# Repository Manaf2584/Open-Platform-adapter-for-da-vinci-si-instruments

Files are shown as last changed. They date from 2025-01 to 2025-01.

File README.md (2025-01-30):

# Bill of Materials

| Item Name | Quantity | Total Cost (£ - GBP) | Description |
|-----------|----------|----------------------|-------------|
| **Dynamixel XC330-M288-T** | 4 | 335.60 | Servo Motors |
| **Igus Linear Guide Carriage TW-04-15** | 2 | 57.98 | Secures servo motor grippers with the servo motors |
| **Igus Linear Guide Rail TS-04-15-600** | 1 | 40.66 | Secures all that is on the Carriage, 13mm |
| **OpenRB-150 Controller** | 1 | 29.10 | Microcontroller |
| **Compression Springs** | 4 | 11.48 | Dimensions: OD=9mm, FL=5mm, Th=0.8mm |
| **SparkFun Joystick** | 1 | 1.04 | Control system |
| **Solderable Breadboard** | 1 | 4.73 | Housed within the control module |
| **Saia-Burgess Plunger Micro Switch (Mfr Part No. 42393)** | 1 | 2.38 | Microswitch, used as a safety switch on the control module |
| **Bambu PLA** | - | - | Print material used for all components |
| **Miscellaneous** | - | 13.53 | 10 kΩ resistor, jumper wires, screws, nuts, heat shrink, thumb screws, and thread inserts |

**Grand Total:** £499.50 (Updated 30/01/2025)

Showcase video: https://youtu.be/XzJ7v7rmKO0

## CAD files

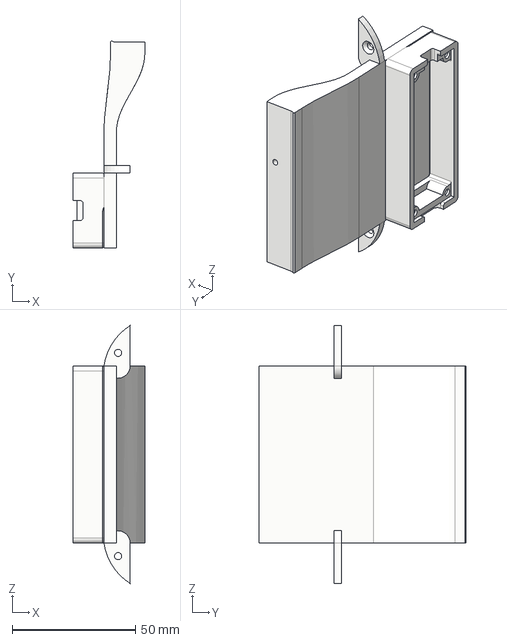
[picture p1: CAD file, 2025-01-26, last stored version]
R Wall.step
29.1 x 83.9 x 104.5 mm

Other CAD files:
R Wall.f3d

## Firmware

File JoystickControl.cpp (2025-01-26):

#include <Dynamixel2Arduino.h>   // Library for controlling Dynamixel motors
#include <tuple>                 // For std::tuple usage
using std::tuple;
using std::make_tuple;
using std::get;

#if defined(ARDUINO_OpenRB)  // If using the OpenRB-150 board
  #define DXL_SERIAL Serial1
  #define DEBUG_SERIAL Serial
  const int DXL_DIR_PIN = -1;
#endif

//----------------------------------
// Function Prototypes
//----------------------------------
tuple<int, int> homeMotor(int DXL_ID);
bool detectNoMovementWithinTurns(int DXL_ID, int delay_time, int no_movement_threshold, int movement_threshold, int max_position_units);
void calculateErrors(); // (Currently unused - for future error calculations)
int scaleToMotorRange(double angle, int cw_limit, int ccw_limit);
void initializeThetas();

//----------------------------------
// Joystick and Switch Configuration
//----------------------------------
const int JOYSTICK_X_PIN = A0;    // X-axis analog pin
const int JOYSTICK_Y_PIN = A1;    // Y-axis analog pin
const int JOYSTICK_SW_PIN = A2;   // Joystick switch pin
const int ENABLE_SWITCH_PIN = A3; // Additional switch pin

// Joystick center values and dead zones
const int JOYSTICK_CENTER_X = 732;
const int JOYSTICK_CENTER_Y = 756;
const int JOYSTICK_CENTER_RANGE_X_MIN = 731;
const int JOYSTICK_CENTER_RANGE_X_MAX = 733;
const int JOYSTICK_CENTER_RANGE_Y_MIN = 755;
const int JOYSTICK_CENTER_RANGE_Y_MAX = 757;
const int JOYSTICK_DEADZONE = 100;

// Control angles and increments
const float MAX_ANGLE_INCREMENT_ROLL_PITCH = 10.0; // deg/update
const float MAX_ANGLE_INCREMENT_JAWS = 10.0;       // deg/update
bool jawControlMode = false;                       // Toggles between roll/pitch mode and jaw mode
bool previousSWState = HIGH;                       // Tracks previous switch state

//----------------------------------
// Dynamixel Configuration
//----------------------------------
const uint8_t DXL_IDs[] = {1, 2, 3, 4};            // Motor IDs
const int NUM_MOTORS = sizeof(DXL_IDs) / sizeof(DXL_IDs[0]);
const float DXL_PROTOCOL_VERSION = 2.0;
const int DXL_BAUD_RATE = 57600;
Dynamixel2Arduino dxl(DXL_SERIAL, DXL_DIR_PIN);

//----------------------------------
// Motion and Safety Limits
//----------------------------------
using namespace ControlTableItem;
const int MAX_CURRENT = 170;  // Safe current limit for motors (in milliamps)
const float MAX_POSITION_RANGE = 600; // Max range in degrees (for safety)
const bool POSITIVE_IS_CCW = true;    // Rotation sign convention

// Arrays to store motor CW/CCW limits (updated after homing)
int cw_limits[NUM_MOTORS];
int ccw_limits[NUM_MOTORS];

//----------------------------------
// Transmission Matrix
//----------------------------------
// Maps user input (theta_R, theta_W, etc.) to motor angles
double transmissionMatrix[4][4] = {
  {0,    0,    0,    1.54},
  {0,    0,    1.03, 0   },
  {0,    1.15, -0.743,0  },
  {1.15, 0,    -0.743,0  }
};

// Inverse of the above matrix to compute motor angles from desired angles
double inverseMatrix[4][4] = {
  {0,               0.6272688898269312, 0,               0.8695652173913043},
  {0,               0.6272688898269312, 0.8695652173913043, 0             },
  {0,               0.970873786407767,  0,               0               },
  {0.6493506493506493, 0,               0,               0               }
};

//----------------------------------
// Angle Variables
//----------------------------------
double theta_R;  // Roll
double theta_W;  // Wrist (pitch)
double theta_G1; // Gripper half 1
double theta_G2; // Gripper half 2

//----------------------------------
// Loop Timing
//----------------------------------
unsigned long lastControlTime = 0;
const unsigned long controlInterval = 40; // in milliseconds

//----------------------------------
// Arduino Setup
//----------------------------------
void setup() {
  delay(1000);
  Serial.begin(57600);

  // Configure joystick and switches
  pinMode(JOYSTICK_SW_PIN, INPUT_PULLUP);
  pinMode(ENABLE_SWITCH_PIN, INPUT_PULLUP);
  previousSWState = digitalRead(JOYSTICK_SW_PIN);

  // Initialize Dynamixel
  dxl.begin(DXL_BAUD_RATE);
  dxl.setPortProtocolVersion(DXL_PROTOCOL_VERSION);

  // Homing sequence for each motor
  for (int i = 0; i < NUM_MOTORS; i++) {
    int DXL_ID = DXL_IDs[i];
    if (dxl.ping(DXL_ID)) {
      Serial.print("Dynamixel with ID: ");
      Serial.print(DXL_ID);
      Serial.println(" is connected!");

      // Set motor to Current Control Mode for homing
      dxl.torqueOff(DXL_ID);
      dxl.setOperatingMode(DXL_ID, OP_CURRENT);
      dxl.writeControlTableItem(CURRENT_LIMIT, DXL_ID, MAX_CURRENT);
      dxl.writeControlTableItem(HOMING_OFFSET, DXL_ID, 0);

      // Home this motor
      tuple<int, int> limits = homeMotor(DXL_ID);
      cw_limits[i] = get<0>(limits);
      ccw_limits[i] = get<1>(limits);
    } 
    else {
      Serial.print("Failed to connect to Dynamixel with ID: ");
      Serial.println(DXL_ID);
    }
  }

  // After homing, set motors to Current-Based Position Mode
  for (int i = 0; i < NUM_MOTORS; i++) {
    int DXL_ID = DXL_IDs[i];
    dxl.torqueOff(DXL_ID);
    dxl.setOperatingMode(DXL_ID, OP_CURRENT_BASED_POSITION);
    dxl.writeControlTableItem(CURRENT_LIMIT, DXL_ID, MAX_CURRENT);
    dxl.torqueOn(DXL_ID);
  }

  // Initialize thetas based on motor positions
  initializeThetas();
}

//----------------------------------
// Main Control Loop
//----------------------------------
void loop() {
  // Ensure the loop runs at a fixed interval
  if (millis() - lastControlTime >= controlInterval) {
    lastControlTime = millis();

    // Detect joystick switch press to toggle jaw mode
    bool currentSWState = digitalRead(JOYSTICK_SW_PIN);
    if (previousSWState == HIGH && currentSWState == LOW) {
      jawControlMode = !jawControlMode;
      Serial.print("Jaw control mode: ");
      Serial.println(jawControlMode ? "ON" : "OFF");
    }
    previousSWState = currentSWState;

    // Read enable switch and joystick
    bool enableSwitchState = digitalRead(ENABLE_SWITCH_PIN);
    int joystickX = analogRead(JOYSTICK_X_PIN);
    int joystickY = analogRead(JOYSTICK_Y_PIN);

    // Check if joystick is near center
    bool isJoystickCentered = 
        (joystickX >= JOYSTICK_CENTER_RANGE_X_MIN && joystickX <= JOYSTICK_CENTER_RANGE_X_MAX) &&
        (joystickY >= JOYSTICK_CENTER_RANGE_Y_MIN && joystickY <= JOYSTICK_CENTER_RANGE_Y_MAX);

    // Only process joystick if switch is not pressed and joystick is not centered
    if (enableSwitchState == HIGH && !isJoystickCentered) {
      int xDeviation = joystickX - JOYSTICK_CENTER_X;
      int yDeviation = joystickY - JOYSTICK_CENTER_Y;

      // Apply deadzone
      if (abs(xDeviation) < JOYSTICK_DEADZONE) xDeviation = 0;
      if (abs(yDeviation) < JOYSTICK_DEADZONE) yDeviation = 0;

      // Update angles if there's significant deviation
      if (xDeviation != 0 || yDeviation != 0) {
        const float MAX_JOYSTICK_DEVIATION = 512 - JOYSTICK_DEADZONE;
        float xAngleIncrement, yAngleIncrement;

        // If jaws are controlled, only horizontal is used by default
        if (jawControlMode) {
          xAngleIncrement = ((float)xDeviation / MAX_JOYSTICK_DEVIATION) * MAX_ANGLE_INCREMENT_JAWS;
          yAngleIncrement = 0; // No vertical by default in jaws mode
        } else {
          // Roll/Pitch control
          xAngleIncrement = ((float)xDeviation / MAX_JOYSTICK_DEVIATION) * MAX_ANGLE_INCREMENT_ROLL_PITCH;
          yAngleIncrement = ((float)yDeviation / MAX_JOYSTICK_DEVIATION) * MAX_ANGLE_INCREMENT_ROLL_PITCH;
        }

        // Update angles based on current mode
        if (jawControlMode) {
          // Jaws: open/close with horizontal movement
          theta_G1 -= xAngleIncrement; 
          theta_G2 += xAngleIncrement;

          // If vertical input is desired for jaws, shift both jaws
          if (yDeviation != 0) {
            float yJawIncrement = ((float)yDeviation / MAX_JOYSTICK_DEVIATION) * MAX_ANGLE_INCREMENT_JAWS;
            double jawsMid = (theta_G1 + theta_G2) / 2.0;
            double jawsHalfGap = (theta_G2 - theta_G1) / 2.0;
            jawsMid += yJawIncrement;
            theta_G1 = jawsMid - jawsHalfGap;
            theta_G2 = jawsMid + jawsHalfGap;
          }

        } else {
          // Roll (theta_R) and Pitch (theta_W)
          theta_R += xAngleIncrement;
          theta_W += yAngleIncrement;
        }

        // Enforce a minimum gap between G1 and G2
        if (theta_G2 > theta_G1) {
          float midAngle = (theta_G1 + theta_G2) / 2;
          theta_G1 = midAngle - 15; 
          theta_G2 = midAngle + 15;
        }

        // Constrain angles to avoid physical damage
        theta_R = constrain(theta_R, -90, 90);
        theta_W = constrain(theta_W, -95, 95);
        theta_G1 = constrain(theta_G1, -200, 190);
        theta_G2 = constrain(theta_G2, -190, 200);
      }
    }

    // Convert degrees to radians
    double theta_R_rad = theta_R * PI / 180.0;
    double theta_W_rad = theta_W * PI / 180.0;
    double theta_G1_rad = theta_G1 * PI / 180.0;
    double theta_G2_rad = theta_G2 * PI / 180.0;

    // Desired joint angles in array form
    double desiredAngles[4] = {theta_R_rad, theta_W_rad, theta_G1_rad, theta_G2_rad};
    double motorAngles[4] = {0};

    // Compute motor angles using the inverse transmission matrix
    for (int i = 0; i < 4; i++) {
      motorAngles[i] = 0;
      for (int j = 0; j < 4; j++) {
        motorAngles[i] += inverseMatrix[i][j] * desiredAngles[j];
      }
    }

    // Convert computed motor angles back to degrees
    for (int i = 0; i < 4; i++) {
      motorAngles[i] *= 180.0 / PI;
    }

    // Scale angles to motor positions
    int motor_positions[NUM_MOTORS];
    motor_positions[0] = scaleToMotorRange(motorAngles[2], cw_limits[0], ccw_limits[0]); // Motor ID 1
    motor_positions[1] = scaleToMotorRange(motorAngles[1], cw_limits[1], ccw_limits[1]); // Motor ID 2
    motor_positions[2] = scaleToMotorRange(motorAngles[0], cw_limits[2], ccw_limits[2]); // Motor ID 3
    motor_positions[3] = scaleToMotorRange(motorAngles[3], cw_limits[3], ccw_limits[3]); // Motor ID 4

    // Send positions and current limit to each motor
    for (int i = 0; i < NUM_MOTORS; i++) {
      dxl.setGoalPosition(DXL_IDs[i], motor_positions[i]);
      dxl.setGoalCurrent(DXL_IDs[i], MAX_CURRENT);
    }
  }
}

//----------------------------------
// Utility Functions
//----------------------------------

/**
 * @brief Scales a given angle (degrees) to the motor's position range.
 */
int scaleToMotorRange(double angle, int cw_limit, int ccw_limit) {
  // Convert angle (deg) to raw position
  int position = angle * 4096 / 360.0;

  int effective_range = abs(ccw_limit - cw_limit);
  int center_position = (cw_limit + ccw_limit) / 2;
  int half_range = effective_range / 2;

  // Constrain within half of the effective range
  position = constrain(position, -half_range, half_range);

  // Adjust sign based on POSITIVE_IS_CCW
  int scaled_position;
  if (POSITIVE_IS_CCW) {
    scaled_position = center_position + position;
  } else {
    scaled_position = center_position - position;
  }
  return scaled_position;
}
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
